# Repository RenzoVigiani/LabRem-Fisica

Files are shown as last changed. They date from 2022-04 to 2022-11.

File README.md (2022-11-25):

# Laboratorios de Física básica
En este readme se detallan las partes mas importantes del proyecto de remotización del laboratorio de física básica, haciendo énfacis en el hardware.

## Protocolo para los laboratorios de "Física básica"
Para poder establecer una comunicación entre al api web, generada por el equipo de software del proyecto, y los dispositivos en el laboratorio establecemos un protocolo en común. 

El procedimiento de comunicación es el siguiente. Cada vez que se quiere modificar algun dato en el laboratorio. El Servidor debe enviar un:
```Ruby 
POST /HTTP/1.1 + <JSON a enviar>
```
#### Json a enviar (ejemplo)
```Ruby  
{ "Estado": [0,true,false],"Analogico": [1,125,542,2]}
```
Y para obtener avances de los datos o reporte de los datos debe enviar un:
```Ruby 
GET /HTTP/1.1
```
De esta forma el Arduino responde ante una petición.

#### Json a recibir (ejemplo)

```Ruby  
{ "Estado": [0,true,false],"Analogico": [1,125,542,2], "Error": "Mensaje de error"}
```

## Sintaxis

**Estado:** Es un array conformado por 3 elementos en el siguiente orden: [Laboratorio, SubLab, Inicio del experimento]

|Laboratorio  | Sub Laboratorio  | Inicio del experimento | Laboratorio Seleccionado | Estado del experimento|
|-|-----|-----|-----------------|--------|
|3|true |true |Lente Convergente|Inicia  |
|3|true |false|Lente Convergente|Finaliza|
|3|false|true |Lente Divergente |Inicia  |
|3|false|false|Lente Divergente |Finaliza|

**Elementos por Laboratorio**

***Convergente***

- Analogico: [Tipo_Diafragma,Distancia_FL,Distancia_LP]
    
    Distancia_FL: Corresponde a la distancia entre Foco y Lente.
    
    Distancia_LP: Corresponde a la distancia entre Lente y Pantalla.

- Tipo_Diafragma = Indica el tipo de diafragma
  - 0 : Sin diafragma
  - 1 : Central
  - 2 : Periferico
  - 3 : Filtro Rojo

***Divergente***

```Ruby 
Analogico:[Tipo_Diafragma, Distancia_FL1, Distancia_L2P, Distancia_L1L2]
```
- Distancia_FL1: Corresponde a la distancia entre Foco y Lente Divergente.
- Distancia_L2P: Corresponde a la distancia entre Lente convergente y Pantalla.
- Distancia_L1L2: Corresponde a la distancia entre Lente divergente y convergente.

## Valores permitidos

Los valores permitidos en las distancias son:

| Distancia          |Valor mín|Valor máx| Unidad |
| ------------------ |---------|---------|--------|
|FL: Foco Lente      |   120   |   970   |  [mm]  |
|LP: Lente Pantalla  |    70   |   970   |  [mm]  |
|FL1: Foco Lente1    |    50   |   920   |  [mm]  |
|L1L2: Lente1 Lente2 |    70   |   900   |  [mm]  |
|L2P: Lente2 Pantalla|    70   |   970   |  [mm]  |

Se puede observar en la imagen las distancias especificadas. Se consideran margenes entre los soportes por seguridad.

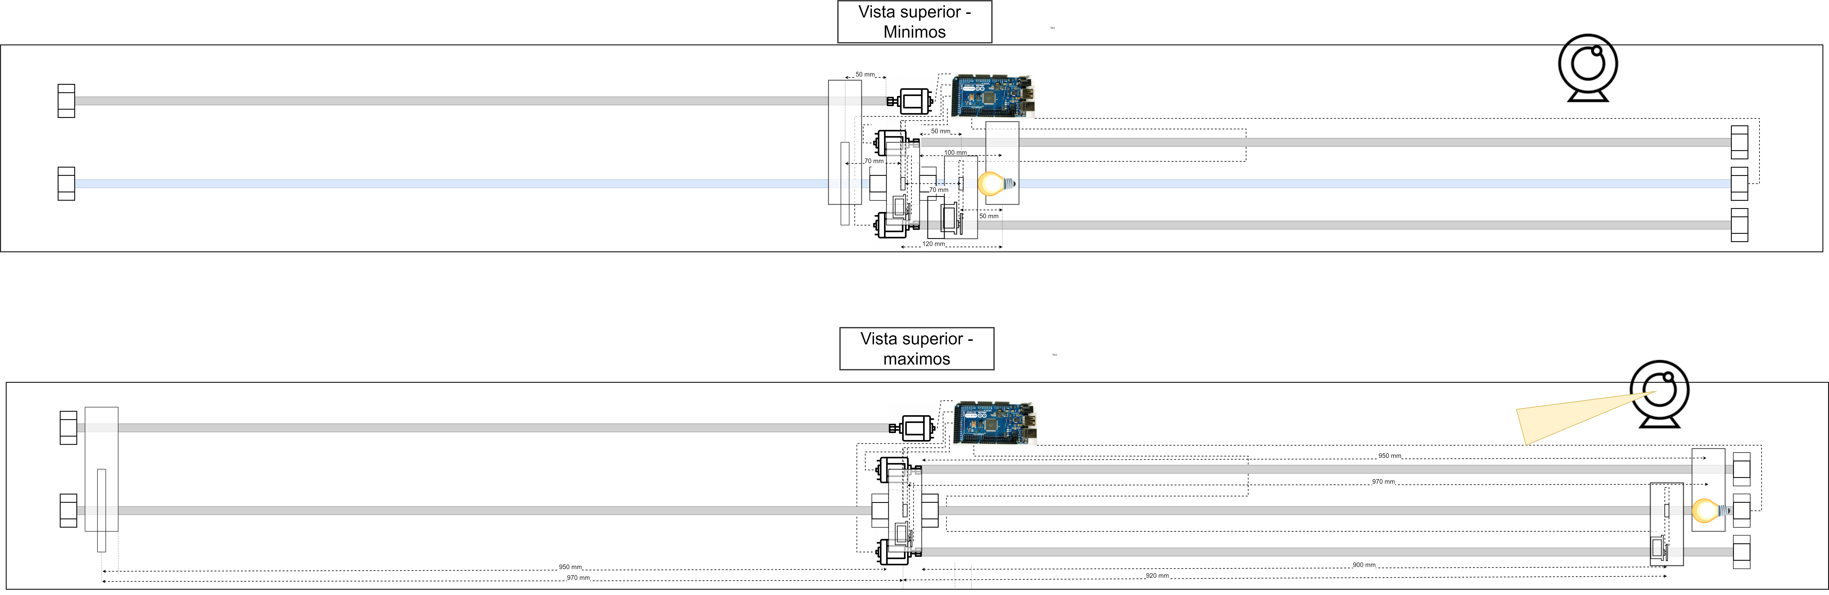
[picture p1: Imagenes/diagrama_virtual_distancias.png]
Vista Superior Distancias


**Error:** Es una variable numerica que representa un mensaje de error. 

| Tipo de error                     |  Valor  |
|-----------------------------------|---------|
| Sin errores                       |    0    |
| Error de distancia                |    1    |
| Error de tipo de diafragma        |    2    |
| Error de laboratorio incorrecto   |    3    |

## Diagramas
Para poder conectar la api web con los actuadores utilizamos un Arduino Mega 2560 y una placa creada por el equipo de hardware. 

Esta placa incorpora todos los drivers e indicadores necesarios para el funcionamiento del laboratorio.

**Arduino Mega 2560: PinOut**
Arduino Mega Pro

||**ESQUEMÁTICO**||
|-|-|-|
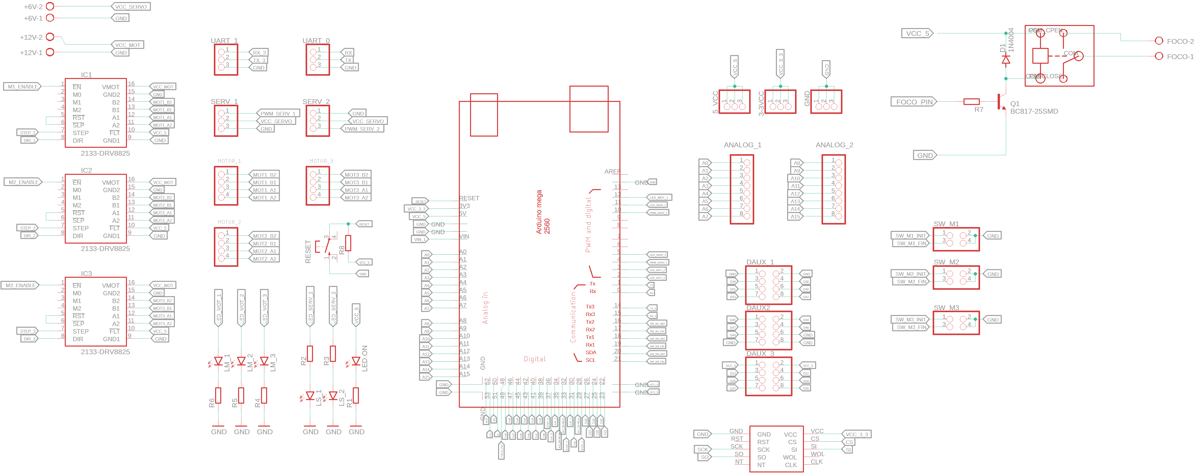
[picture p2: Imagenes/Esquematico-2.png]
Esquematico
||||

||**PCB**||
|-|-|-|
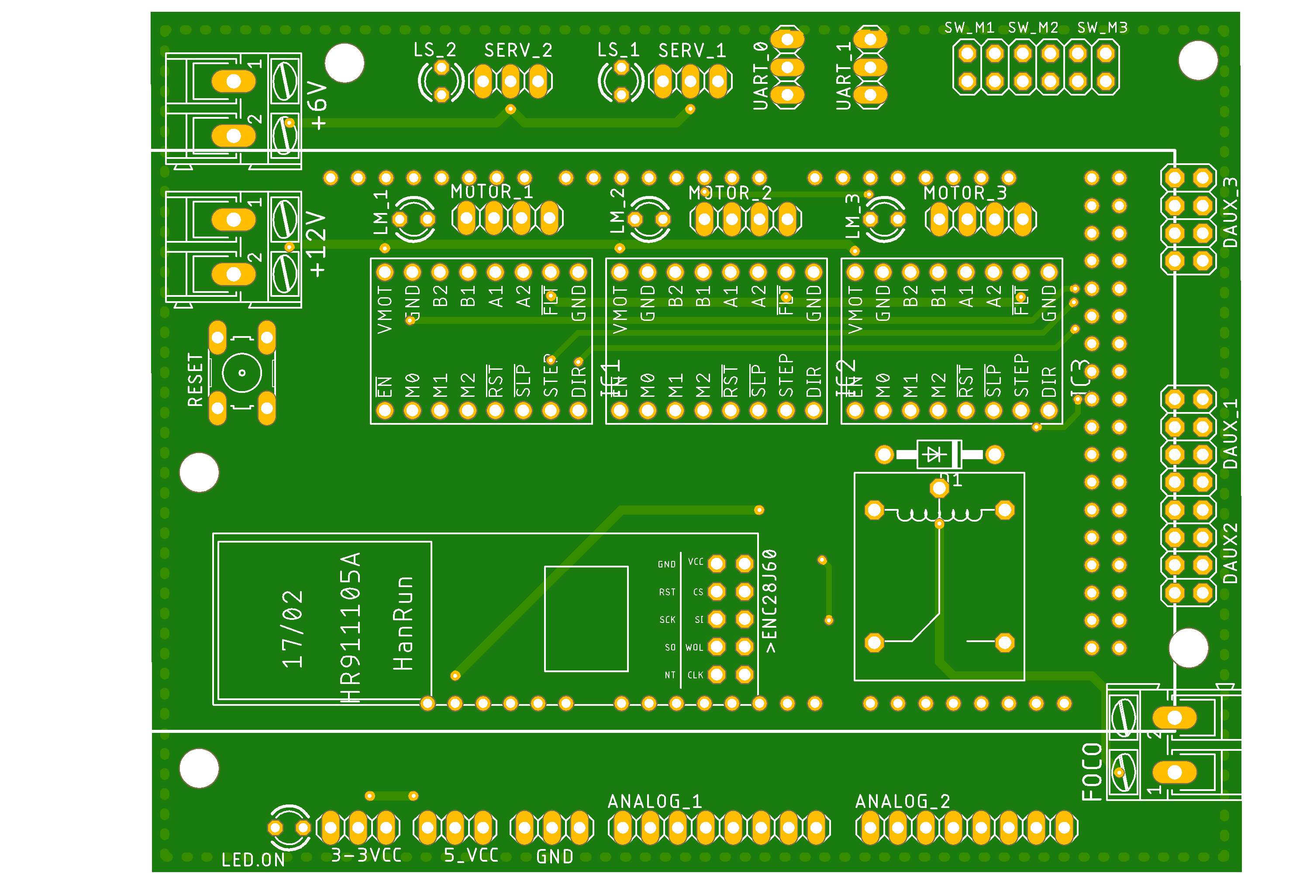
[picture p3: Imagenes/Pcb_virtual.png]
Pcb Virtual
||||
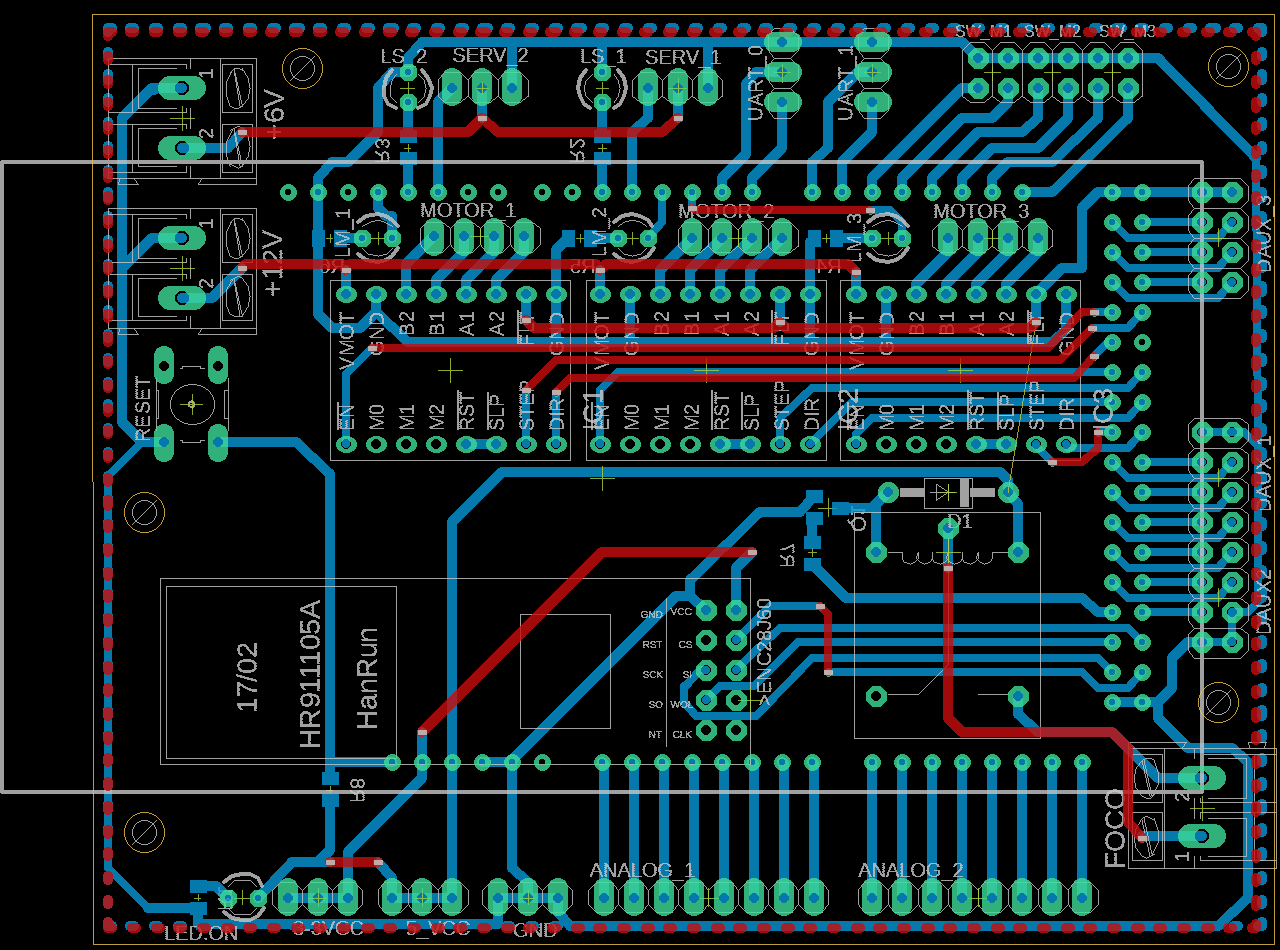
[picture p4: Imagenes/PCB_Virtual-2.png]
Pcb Virtual
||||
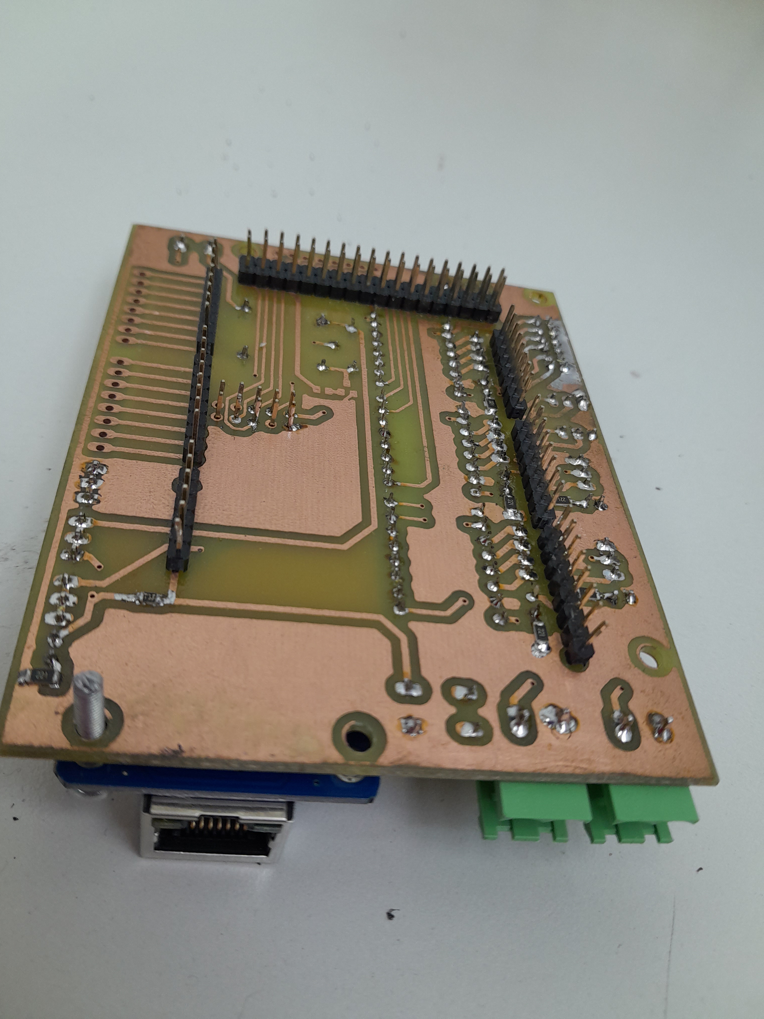
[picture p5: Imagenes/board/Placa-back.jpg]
||||
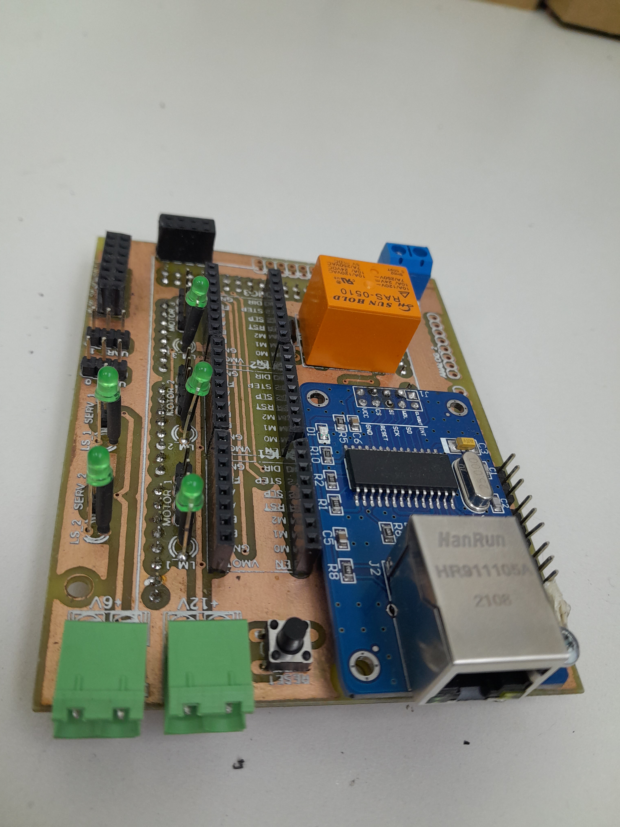
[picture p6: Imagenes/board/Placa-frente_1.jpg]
||||
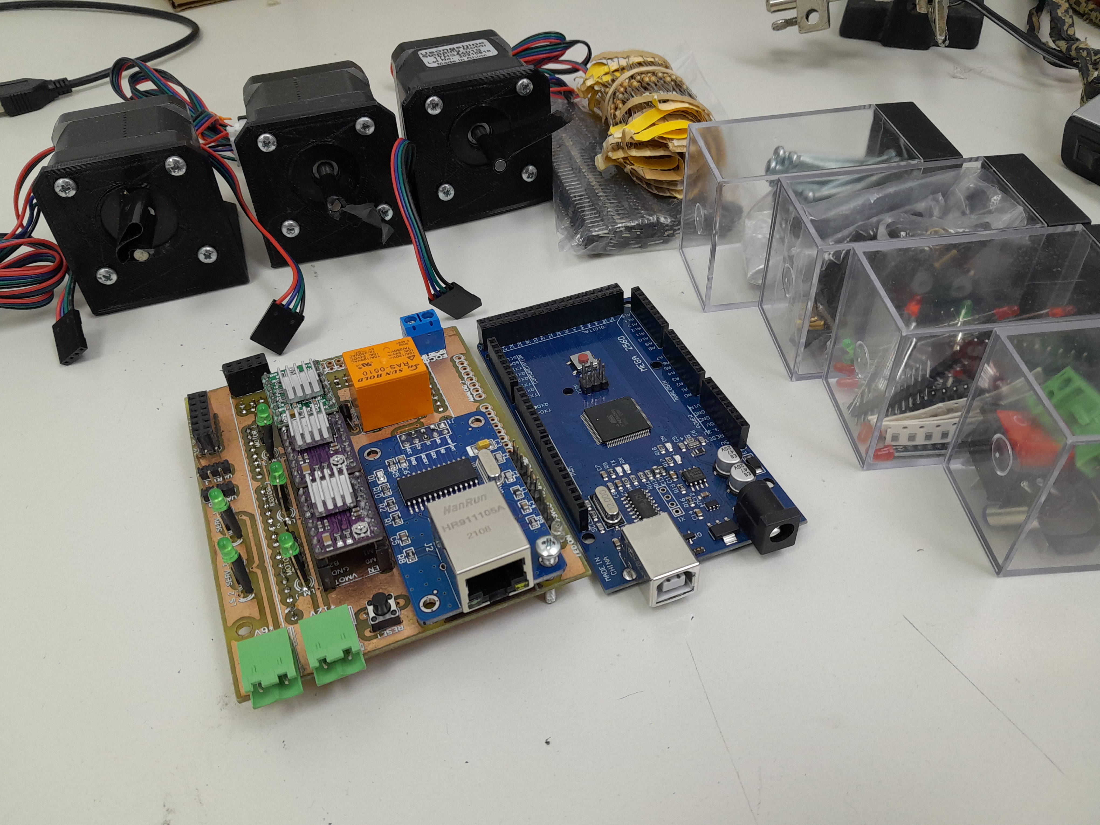
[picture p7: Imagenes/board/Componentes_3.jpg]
||||

**Diagrama general**

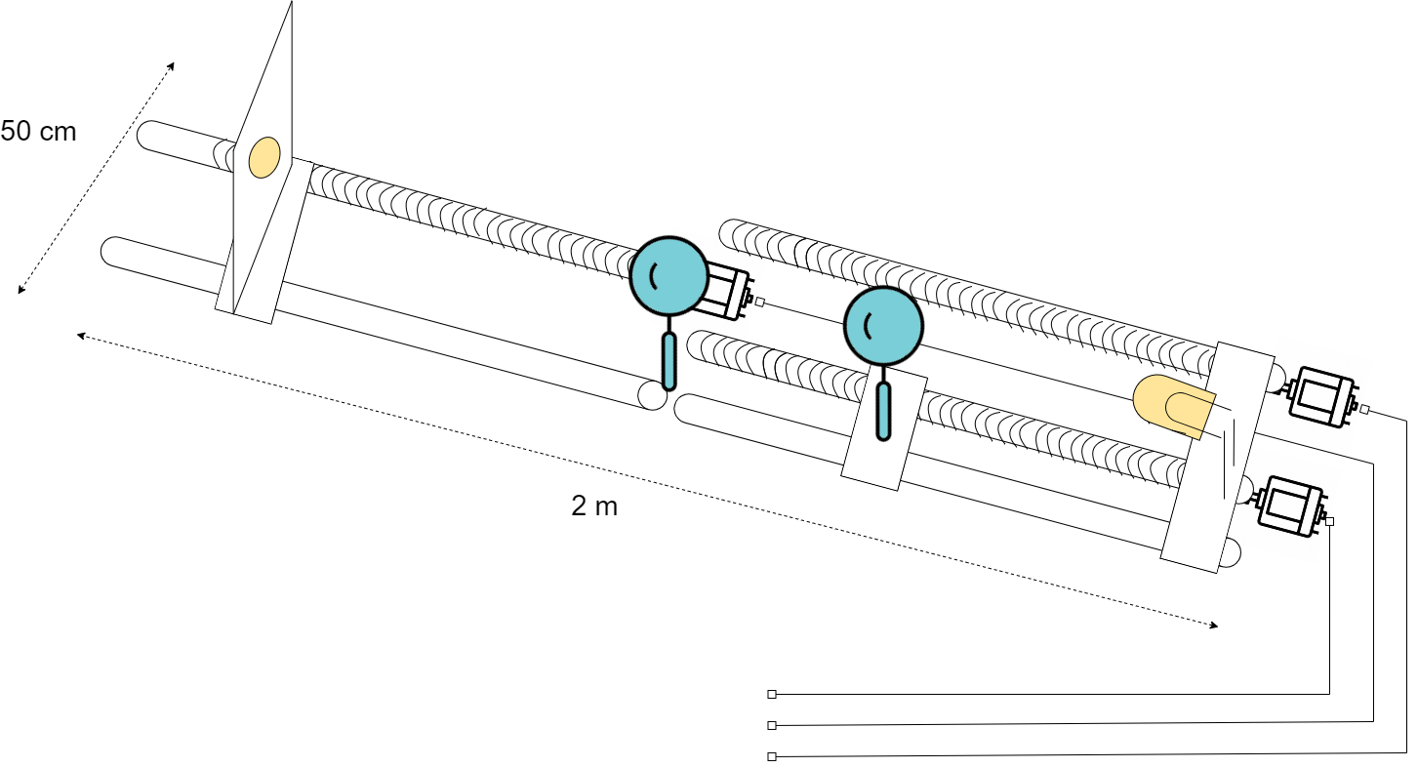
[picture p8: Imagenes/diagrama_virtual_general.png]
Vista General Virtual


**Diagrama Vista superior**

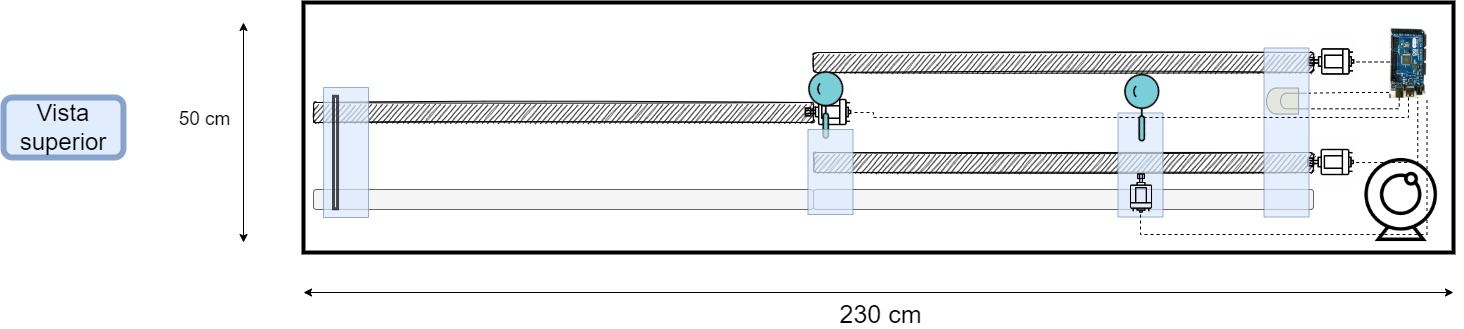
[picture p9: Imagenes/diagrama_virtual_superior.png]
Vista Superior Virtual


**Diagrama Vista frontal**

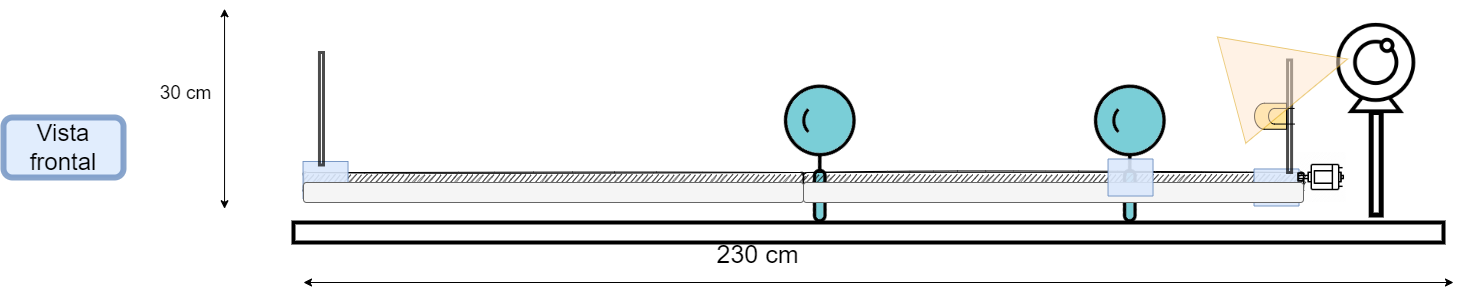
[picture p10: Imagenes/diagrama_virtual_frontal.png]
Vista Frontal Virtual


**Datasheets Actuadores**
- [Recopilación de Datasheets](https://renzovigiani.notion.site/adea4f735c994faaa2f919a7e5105e9d?v=83070c8c05d34c02905fc370e37b802a)
- [Servo Motor MG966R](https://github.com/RenzoVigiani/LabRem-Fisica/blob/main/datasheets/MG996R-Datasheet.pdf)
- [Motor Paso a paso](https://github.com/RenzoVigiani/LabRem-Fisica/blob/main/datasheets/MG996R-Datasheet.pdf)
- [Lampara Led](http://wayjun.com/Datasheet/Led/3W%20High%20Power%20LED.pdf)

**Soportes 3D**

 A continuación se pueden ver los elementos diseñados por el equipo de hardware y luego creados a partir de una impresora 3D. Esto permitió generar soportes y gabinetes de acuerdo a los requerimientos y logrando mayor flexibilidad.

Se pueden ver los soportes creados para el sistema de movimiento de todo el ensayo. Se muestran:
- 4 bases para las lentes y el movimiento sobre los rieles.
- 3 soportes para motores paso a paso.
- 1 gabinete para soporte de foco o fuente de luz.
- 1 soporte para la pantalla.

|            |   |
|-------------------------|---------|
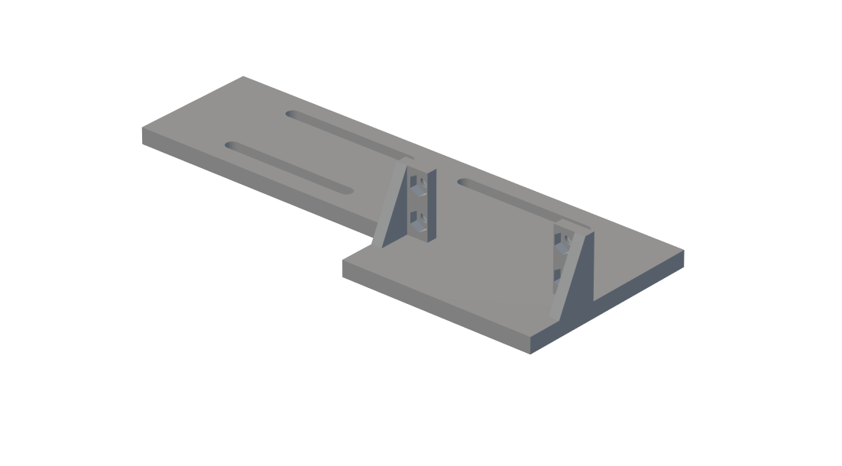
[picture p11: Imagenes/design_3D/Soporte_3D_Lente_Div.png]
Soporte 3D Lente Divergente
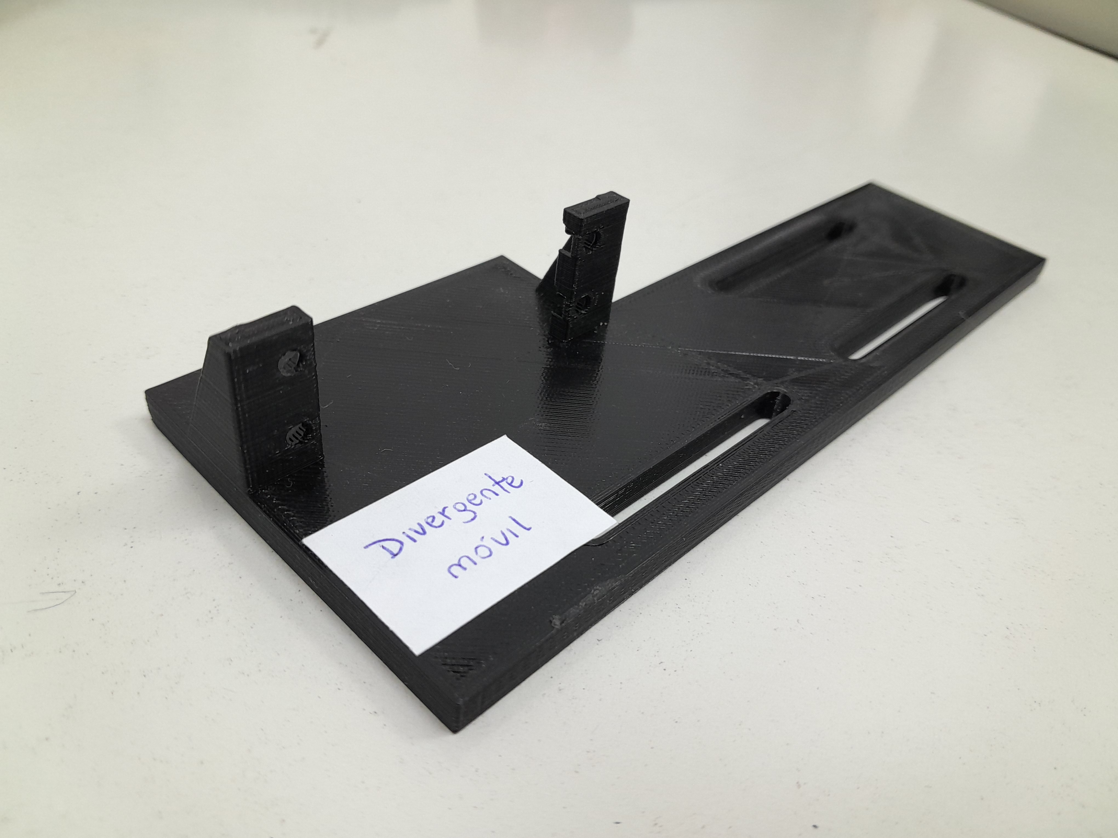
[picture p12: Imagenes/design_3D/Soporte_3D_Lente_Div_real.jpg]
Soporte 3D Lente Divergente Real
|   |    |
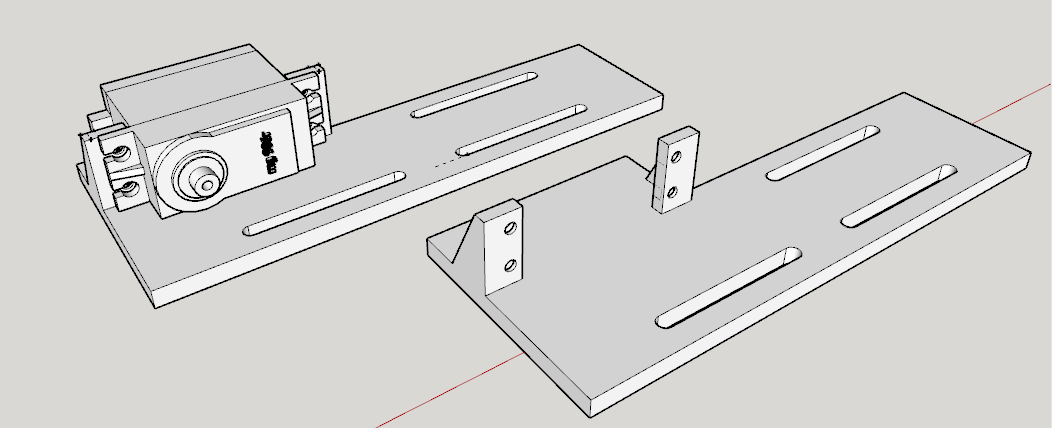
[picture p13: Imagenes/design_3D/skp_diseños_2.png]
Soporte 3D Lente Diafragma
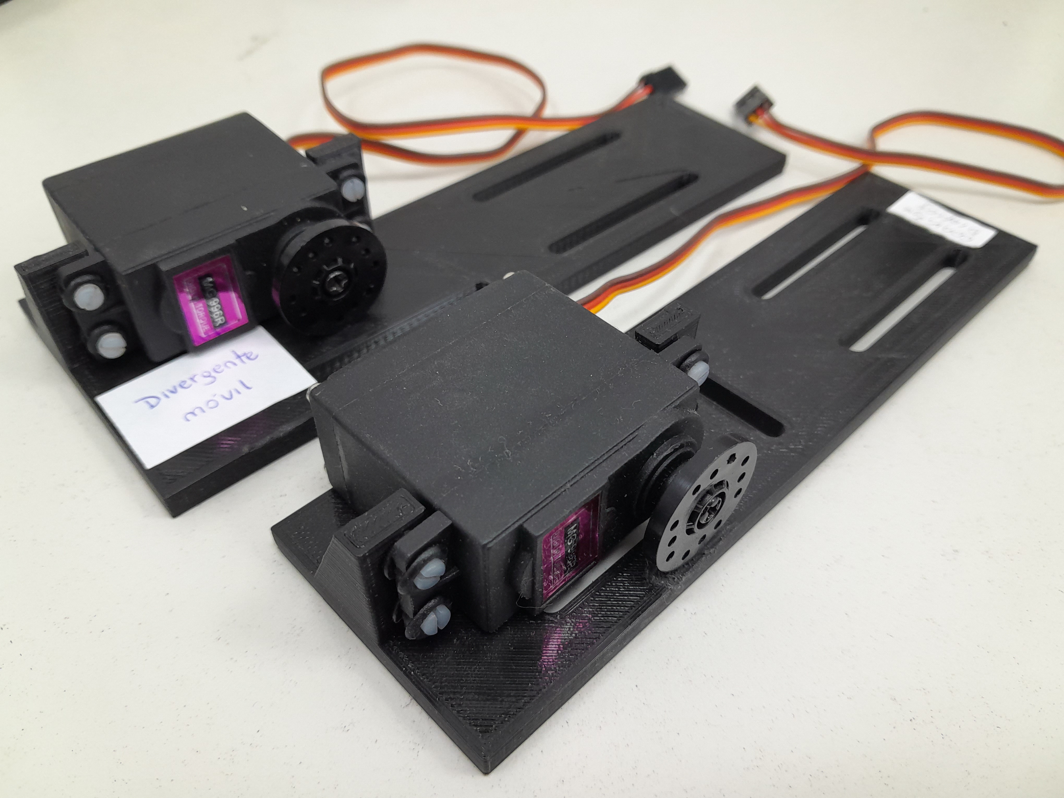
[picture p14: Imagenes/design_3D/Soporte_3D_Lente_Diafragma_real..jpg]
Soporte 3D Lente Diafragma Real
| ||
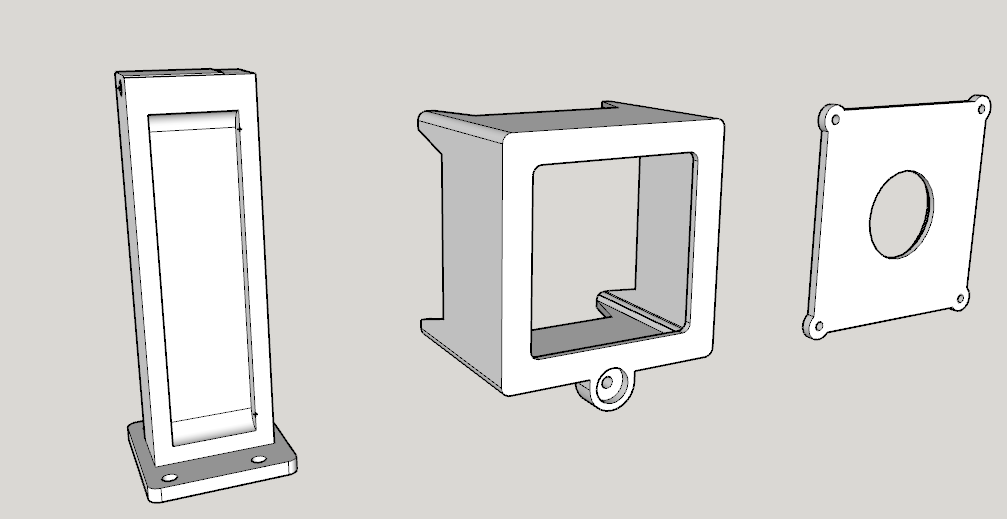
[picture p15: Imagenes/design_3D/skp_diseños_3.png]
Caja Lampara Led
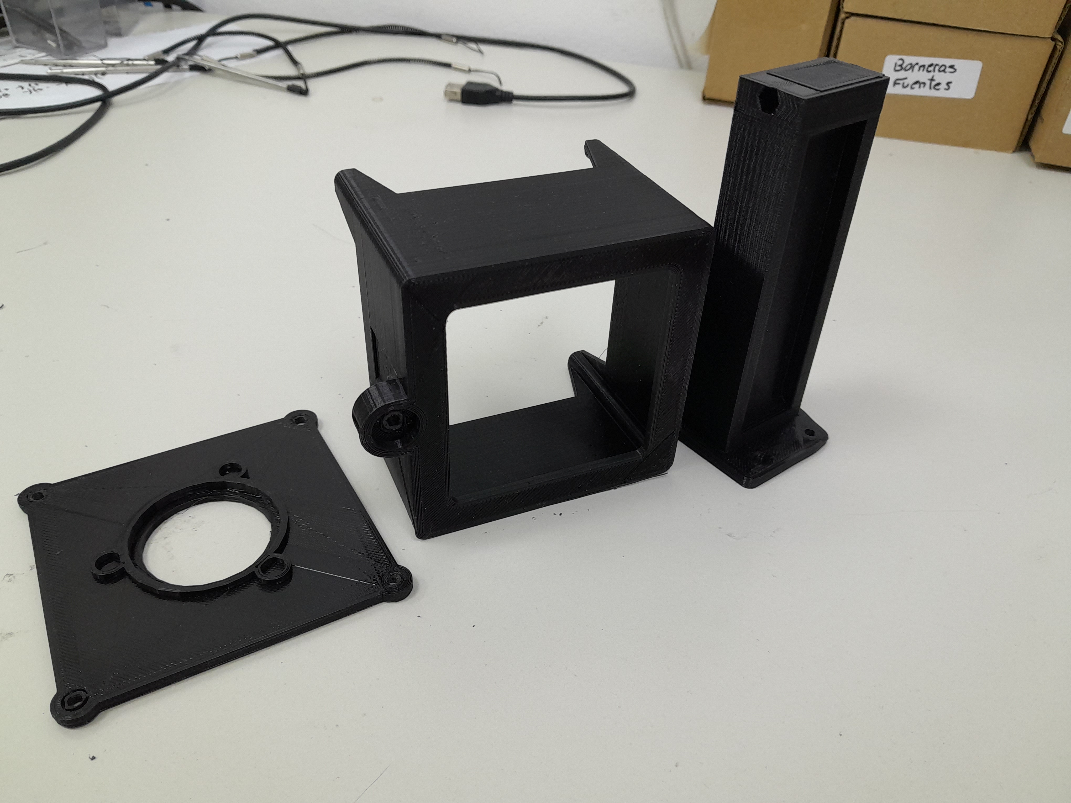
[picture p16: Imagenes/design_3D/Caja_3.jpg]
Caja Lampara Led 2
|   |   |
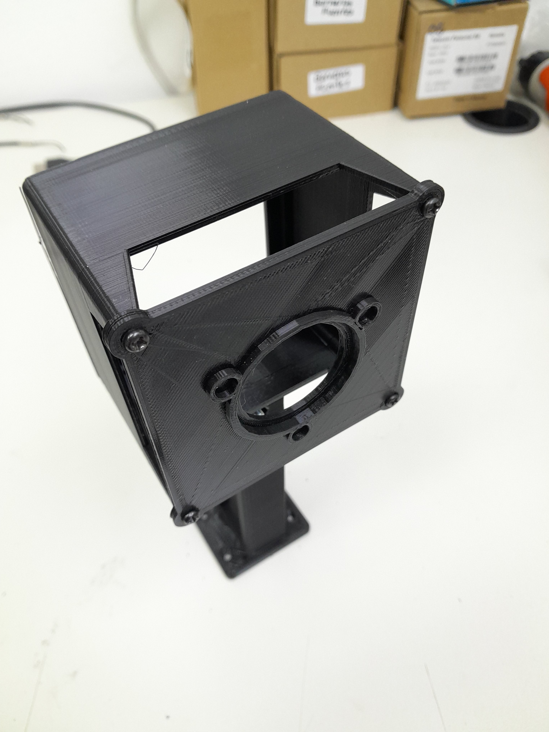
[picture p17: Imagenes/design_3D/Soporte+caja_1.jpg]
Caja Lampara Led Ensamblado
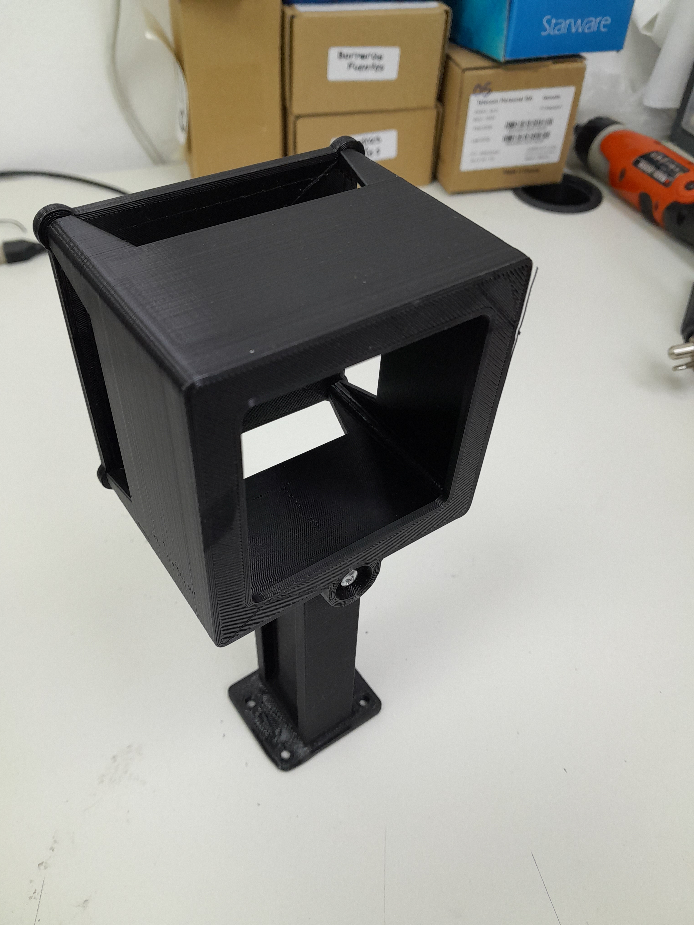
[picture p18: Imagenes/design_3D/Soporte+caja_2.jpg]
Caja Lampara Led Ensamblado 2
|  |  |
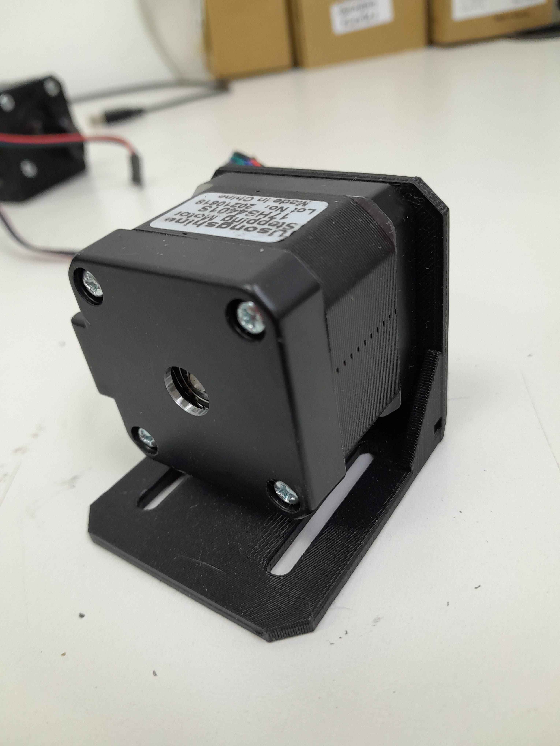
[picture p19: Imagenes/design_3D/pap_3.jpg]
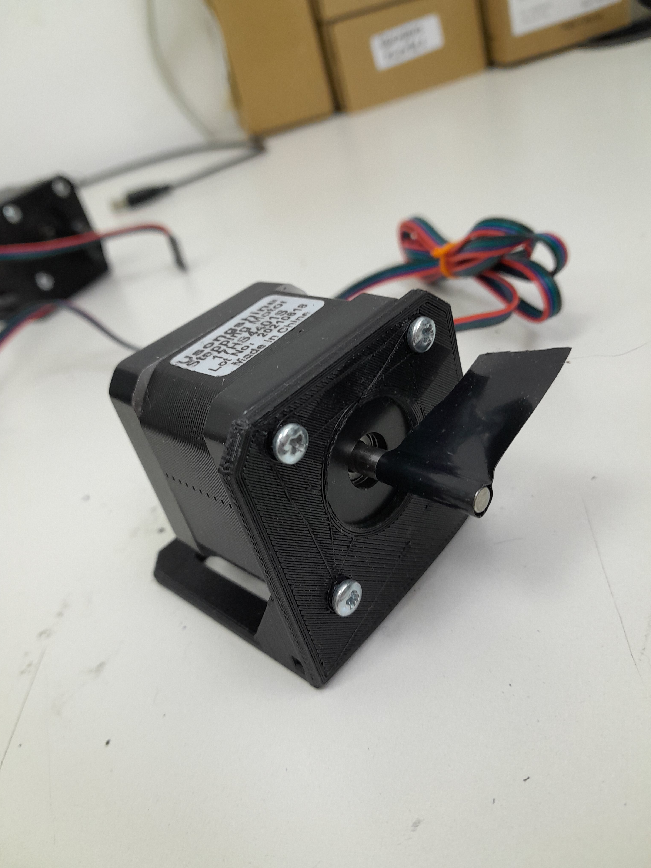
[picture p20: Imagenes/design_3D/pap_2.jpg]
|  |  |
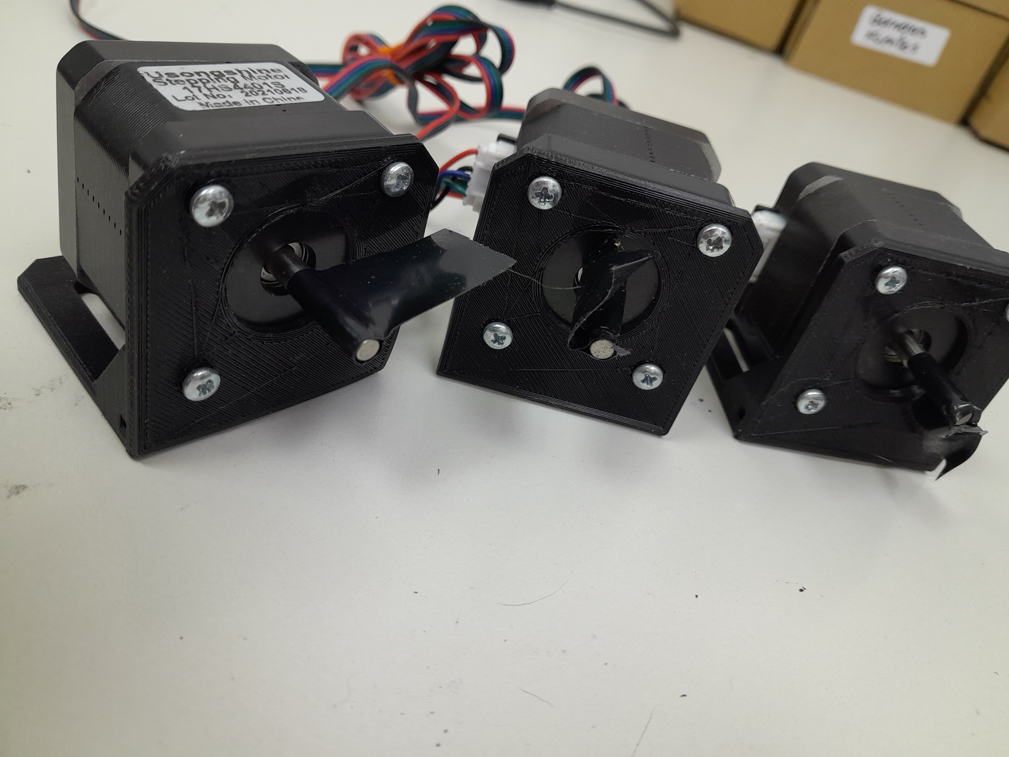
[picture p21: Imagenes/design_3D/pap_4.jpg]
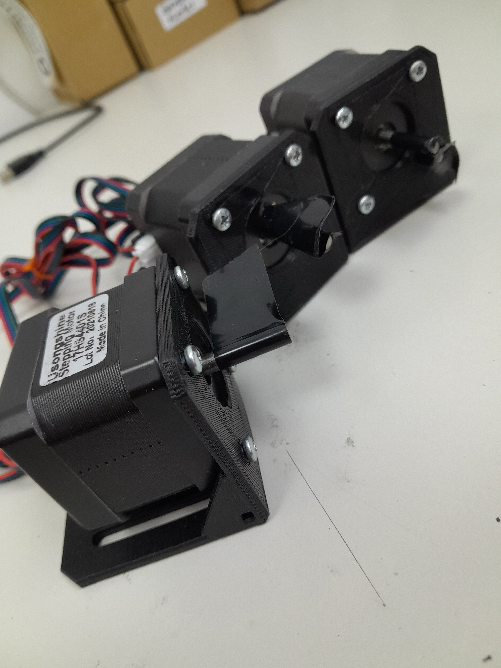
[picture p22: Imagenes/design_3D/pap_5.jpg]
|  |  |

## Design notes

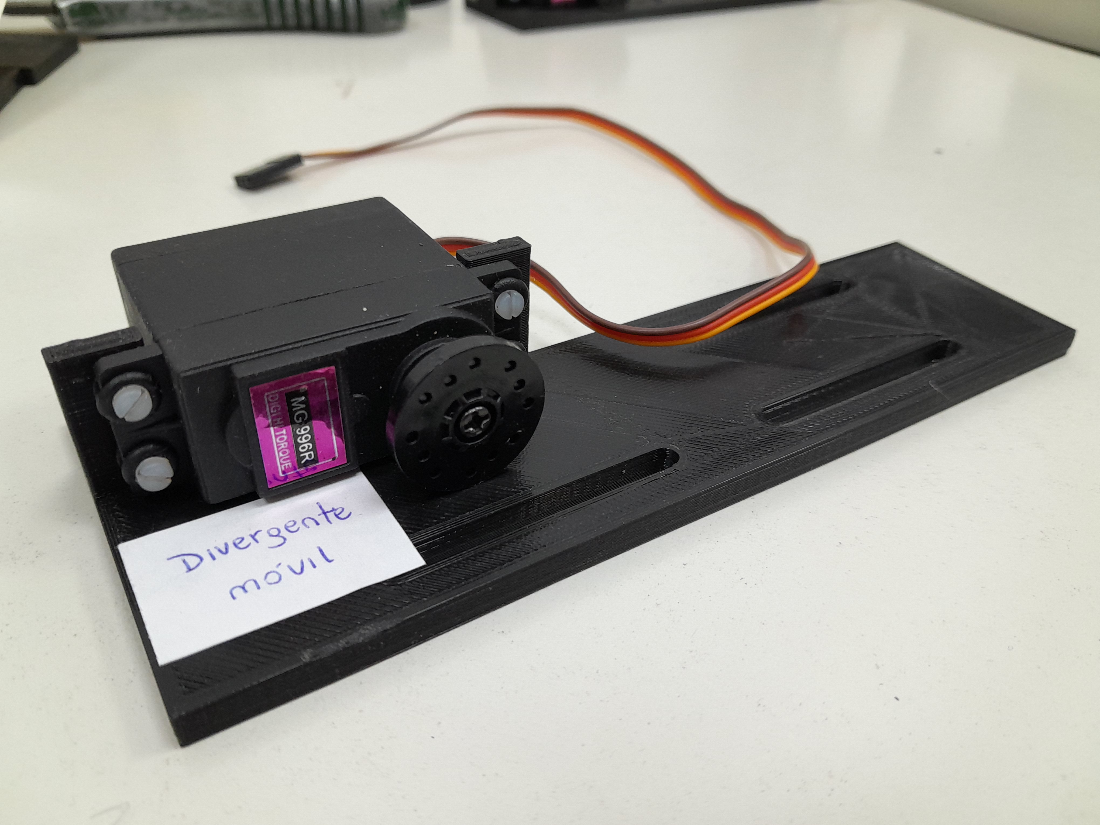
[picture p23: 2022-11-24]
Imagenes/design_3D/Base_servo_2.jpg

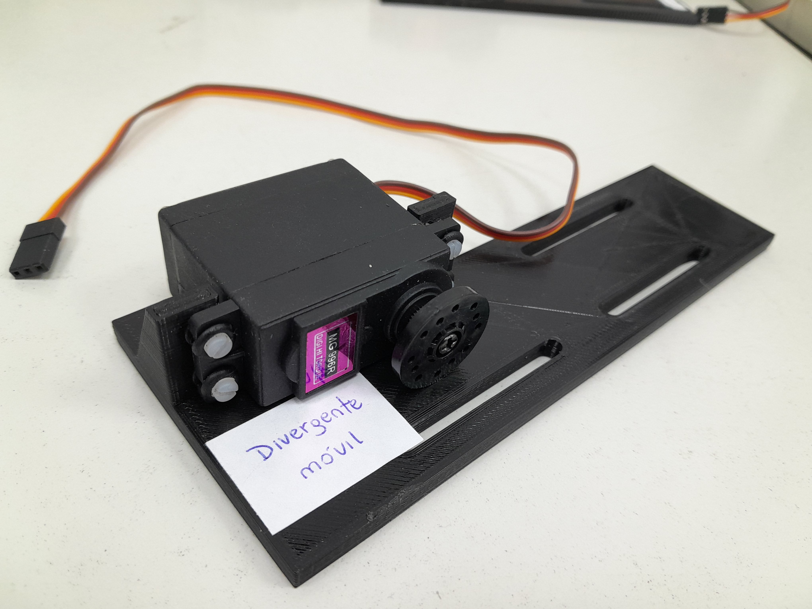
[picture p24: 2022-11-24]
Imagenes/design_3D/Base_servo_3.jpg

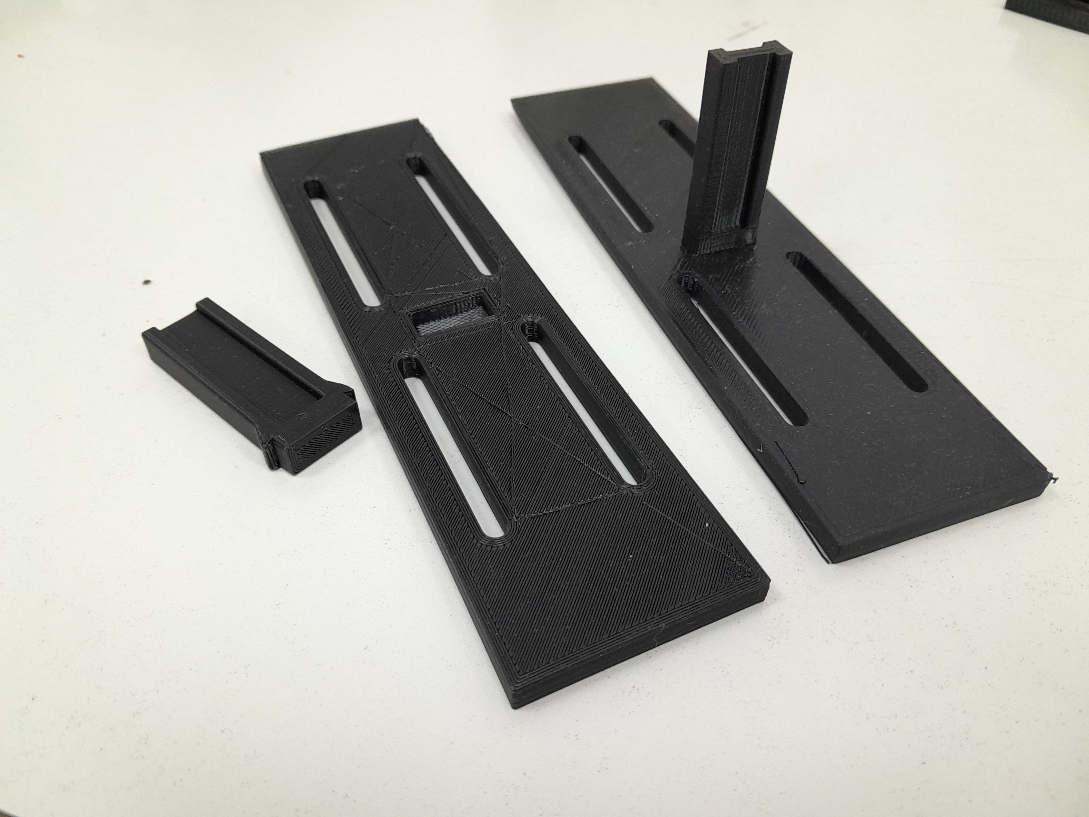
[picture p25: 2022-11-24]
Imagenes/design_3D/Base_lente1.jpg

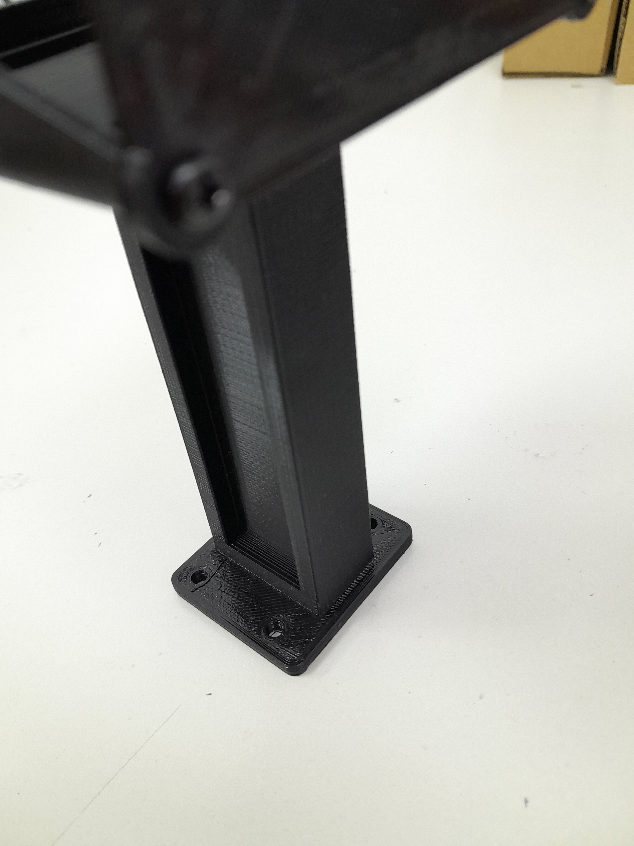
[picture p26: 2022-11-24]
Imagenes/design_3D/Soporte+caja_3.jpg

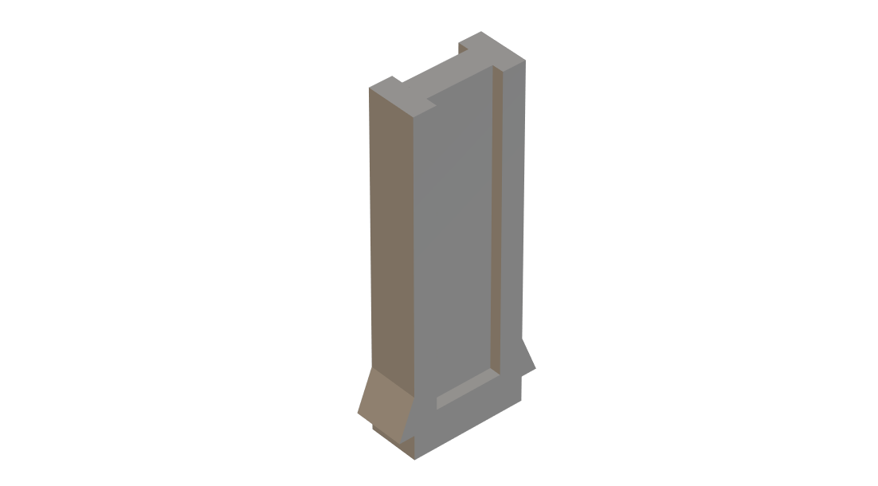
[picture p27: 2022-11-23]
Imagenes/design_3D/Soporte_3D_barra_central.png

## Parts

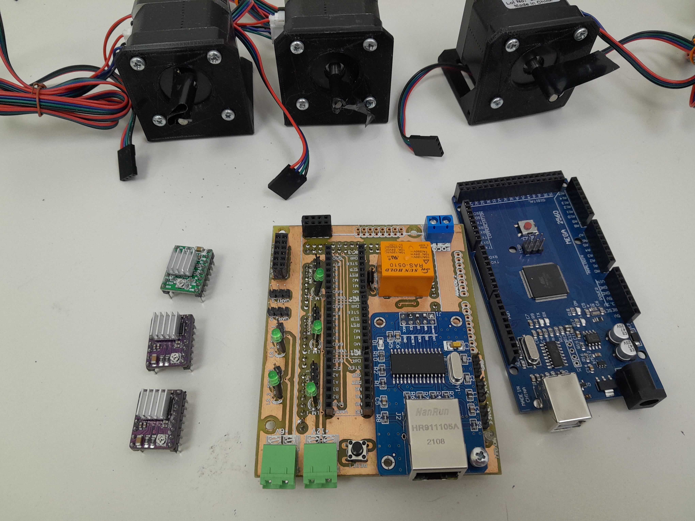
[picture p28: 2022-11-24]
Imagenes/board/Componentes_2.jpg

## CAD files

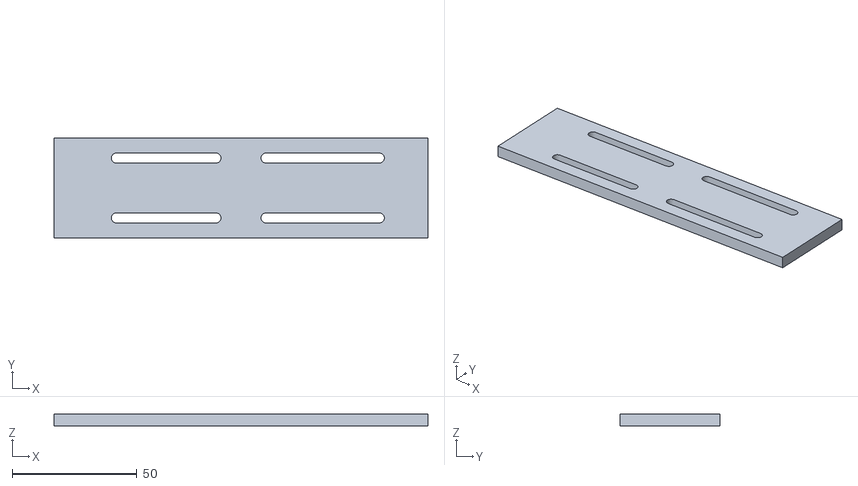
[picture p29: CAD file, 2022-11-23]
Impresion_3D/LuzBarra.stl
150.0 x 40.0 x 5.00

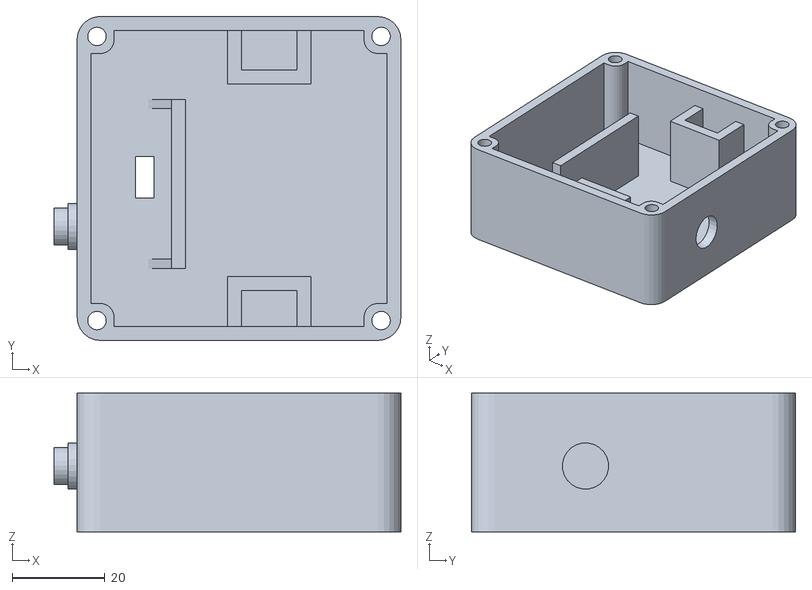
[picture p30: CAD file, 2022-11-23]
Impresion_3D/Caja.stl
75.0 x 70.0 x 30.0

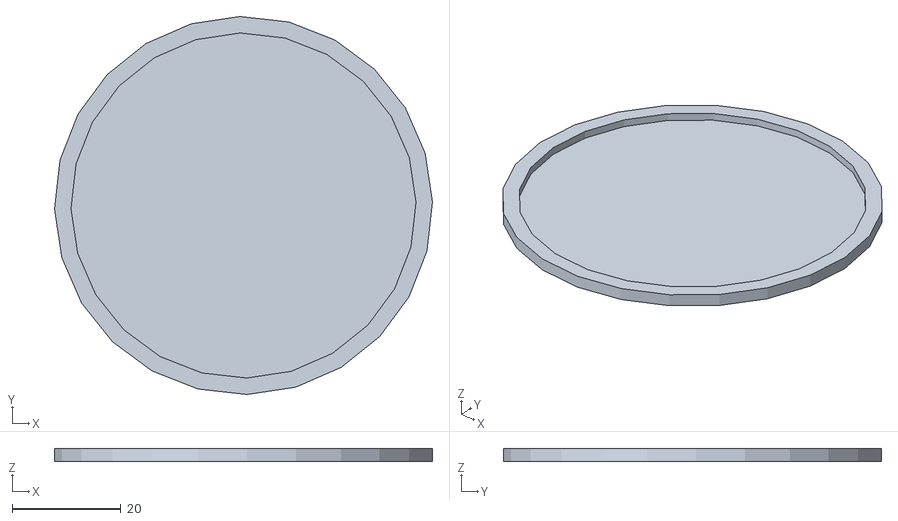
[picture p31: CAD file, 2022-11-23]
Impresion_3D/Difusor.stl
69.4 x 69.4 x 2.30

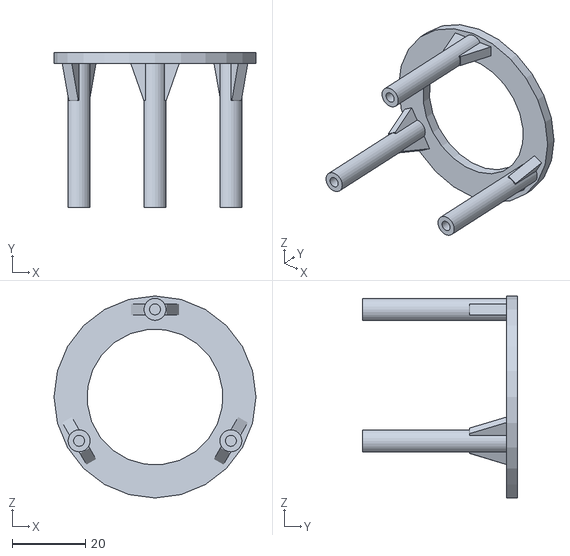
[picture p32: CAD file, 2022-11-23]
Impresion_3D/LuzPorta.stl
55.0 x 42.2 x 55.0

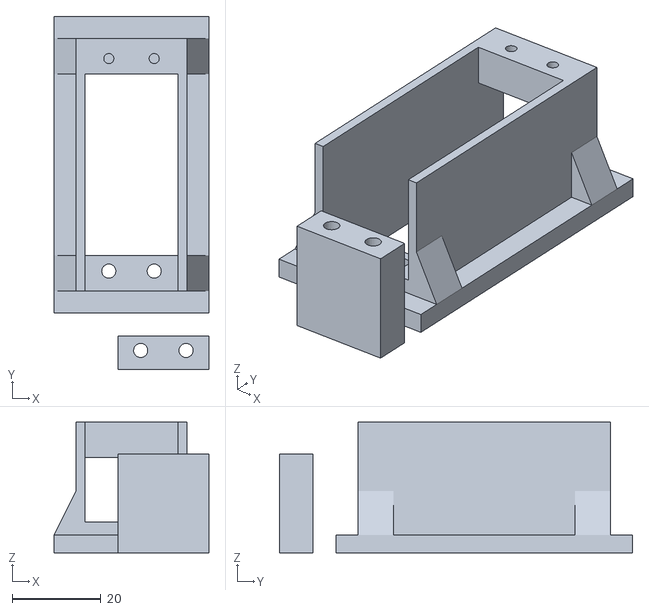
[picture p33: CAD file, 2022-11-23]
Impresion_3D/TelecoServo.stl
35.0 x 79.7 x 29.5

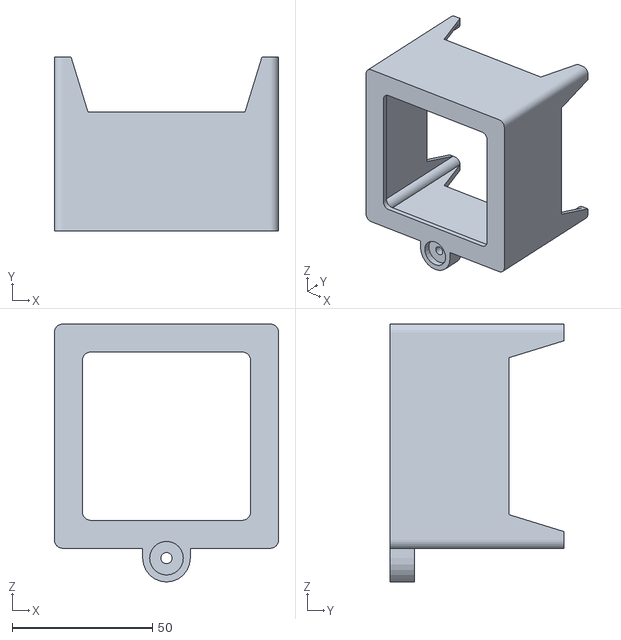
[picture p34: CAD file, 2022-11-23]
Impresion_3D/LuzFrente.stl
80.0 x 61.9 x 92.0

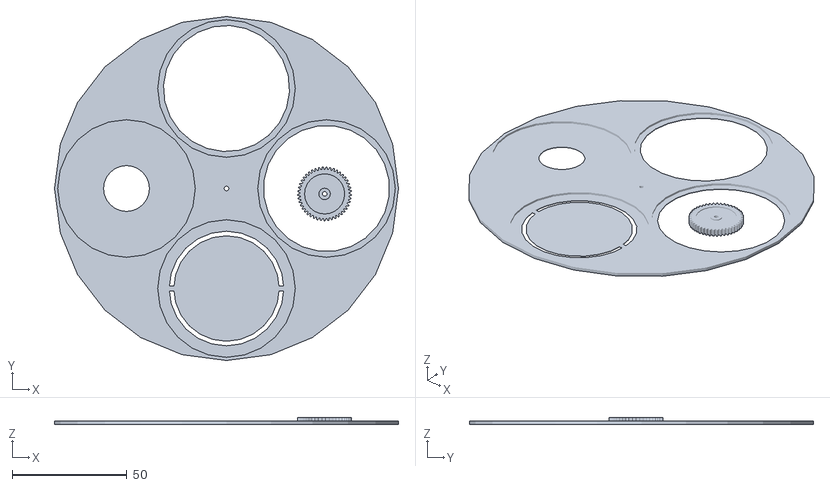
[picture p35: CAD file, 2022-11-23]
Impresion_3D/diafragma-con-engranaje.stl
150.0 x 150.0 x 3.00

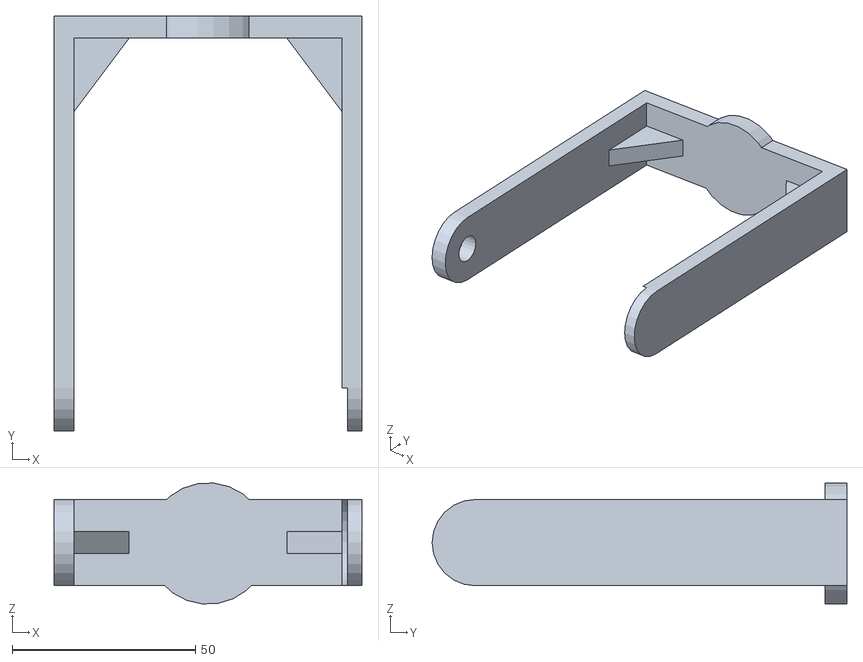
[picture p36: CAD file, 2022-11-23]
Impresion_3D/SoporteCaja.stl
84.0 x 113.1 x 33.0

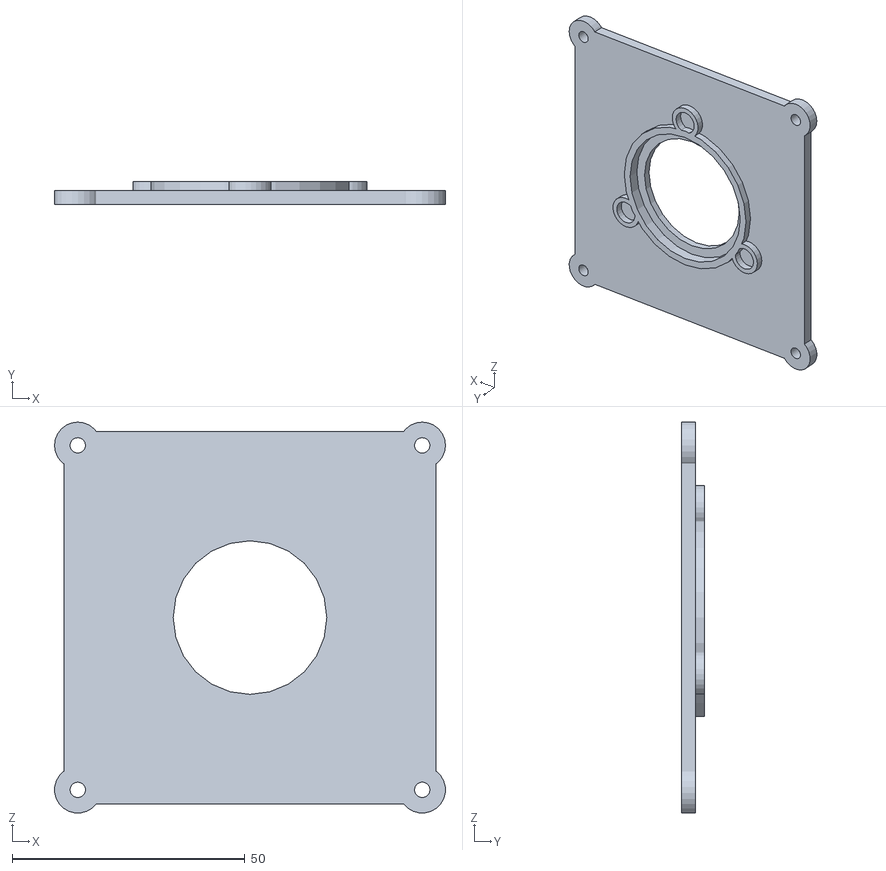
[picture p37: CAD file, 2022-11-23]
Impresion_3D/LuzTrasera.stl
84.0 x 5.00 x 84.0

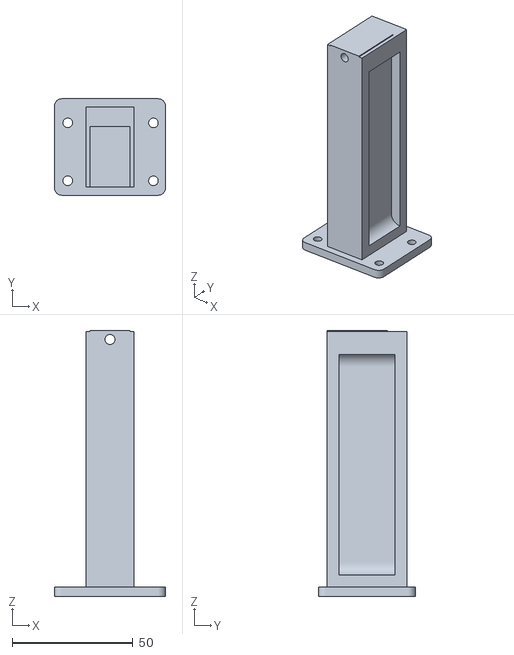
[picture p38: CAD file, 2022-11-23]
Impresion_3D/LuzPoste.stl
46.0 x 40.0 x 110.2

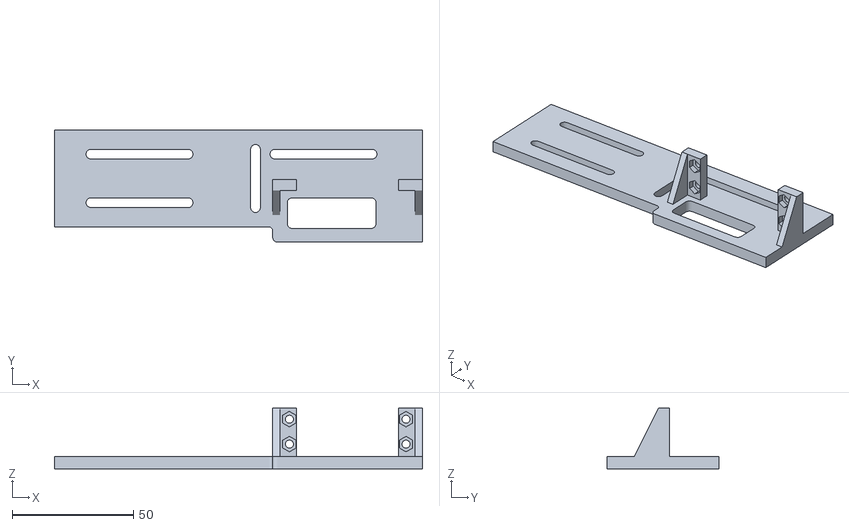
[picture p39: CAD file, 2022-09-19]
Impresion_3D/Barra_10x4_LyD.stl
151.5 x 46.2 x 25.0

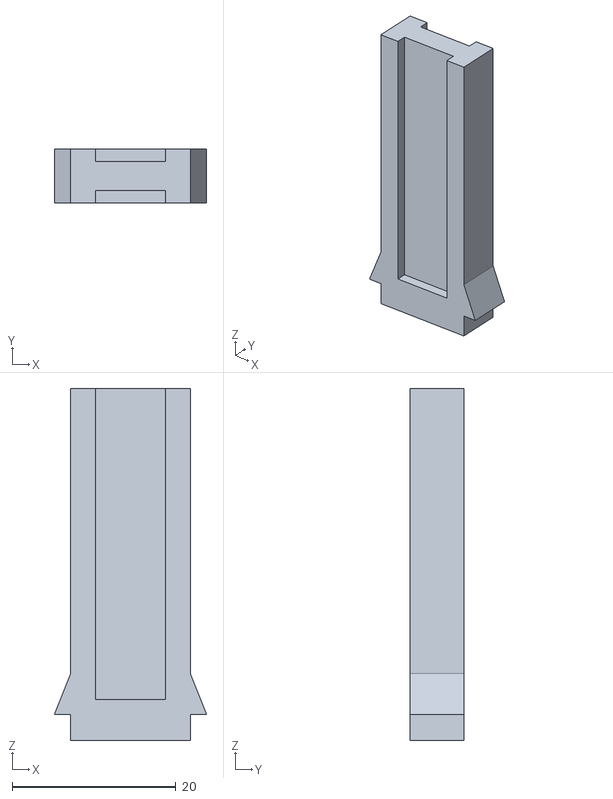
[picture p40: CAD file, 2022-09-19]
Impresion_3D/BarraInterna.stl
18.6 x 6.60 x 43.0

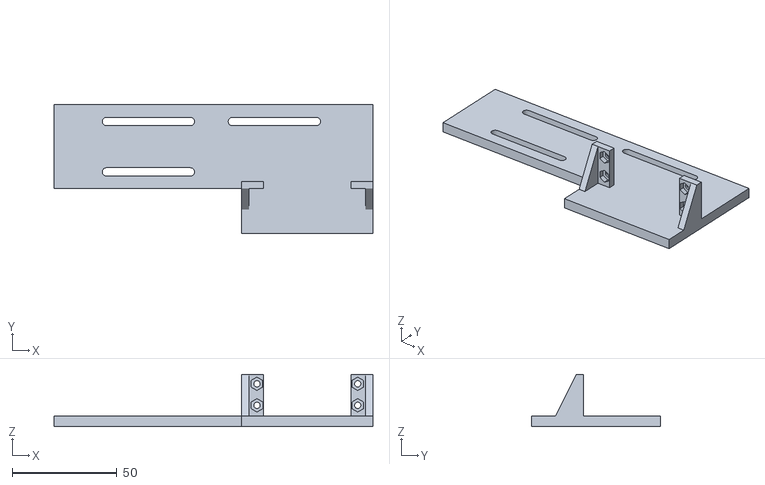
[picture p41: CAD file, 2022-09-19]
Impresion_3D/Barra_10x4_V2.stl
152.0 x 61.2 x 25.0

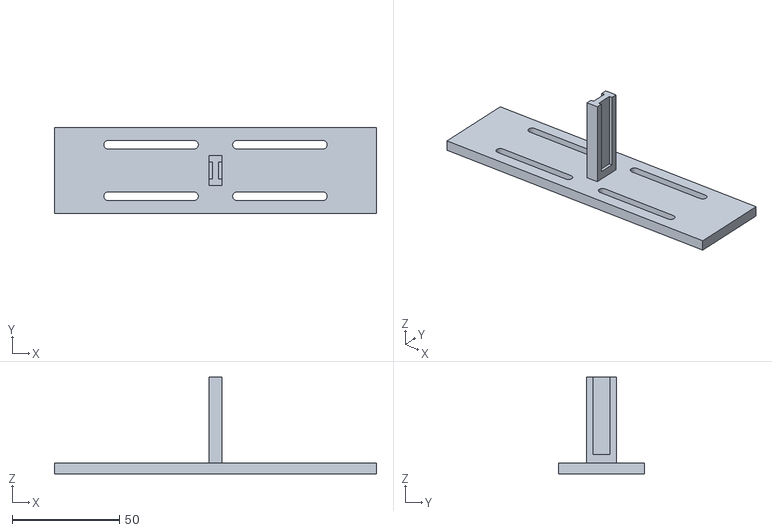
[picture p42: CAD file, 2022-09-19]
Impresion_3D/Barra_15x4.stl
150.0 x 40.0 x 45.0

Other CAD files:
Esquematico_y_PCB/Diseño de FISICA v19.f3z
Esquematico_y_PCB/Diseño de FISICA v2.f3z
Esquematico_y_PCB/Diseño de FISICA v8.f3z
Impresion_3D/14b+engranaje+45+dientes.skp
Impresion_3D/828_DELUX_3D-DRAWINGS.skp
Impresion_3D/BarraInterna.skp
Impresion_3D/Barra_10x4.skp
Impresion_3D/Barra_10x4_LyD.skp
Impresion_3D/Barra_10x4_V2.skp
Impresion_3D/Barra_15x4.skp
Impresion_3D/Caja.skp
Impresion_3D/CajaCompleto.skp
Impresion_3D/Difusor.skp
Impresion_3D/LuzBarra.skp
Impresion_3D/LuzCompleta.skp
Impresion_3D/LuzFisica.skp
Impresion_3D/LuzFrente.skp
Impresion_3D/LuzPorta.skp
Impresion_3D/LuzPoste.skp
Impresion_3D/LuzTrasera.skp
Impresion_3D/SoporteCaja.skp
Impresion_3D/TelecoServo.skp

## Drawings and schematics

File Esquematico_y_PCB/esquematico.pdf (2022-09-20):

# 2133-DRV8825

# BC817-25SMD ¹N⁴⁰⁰⁴

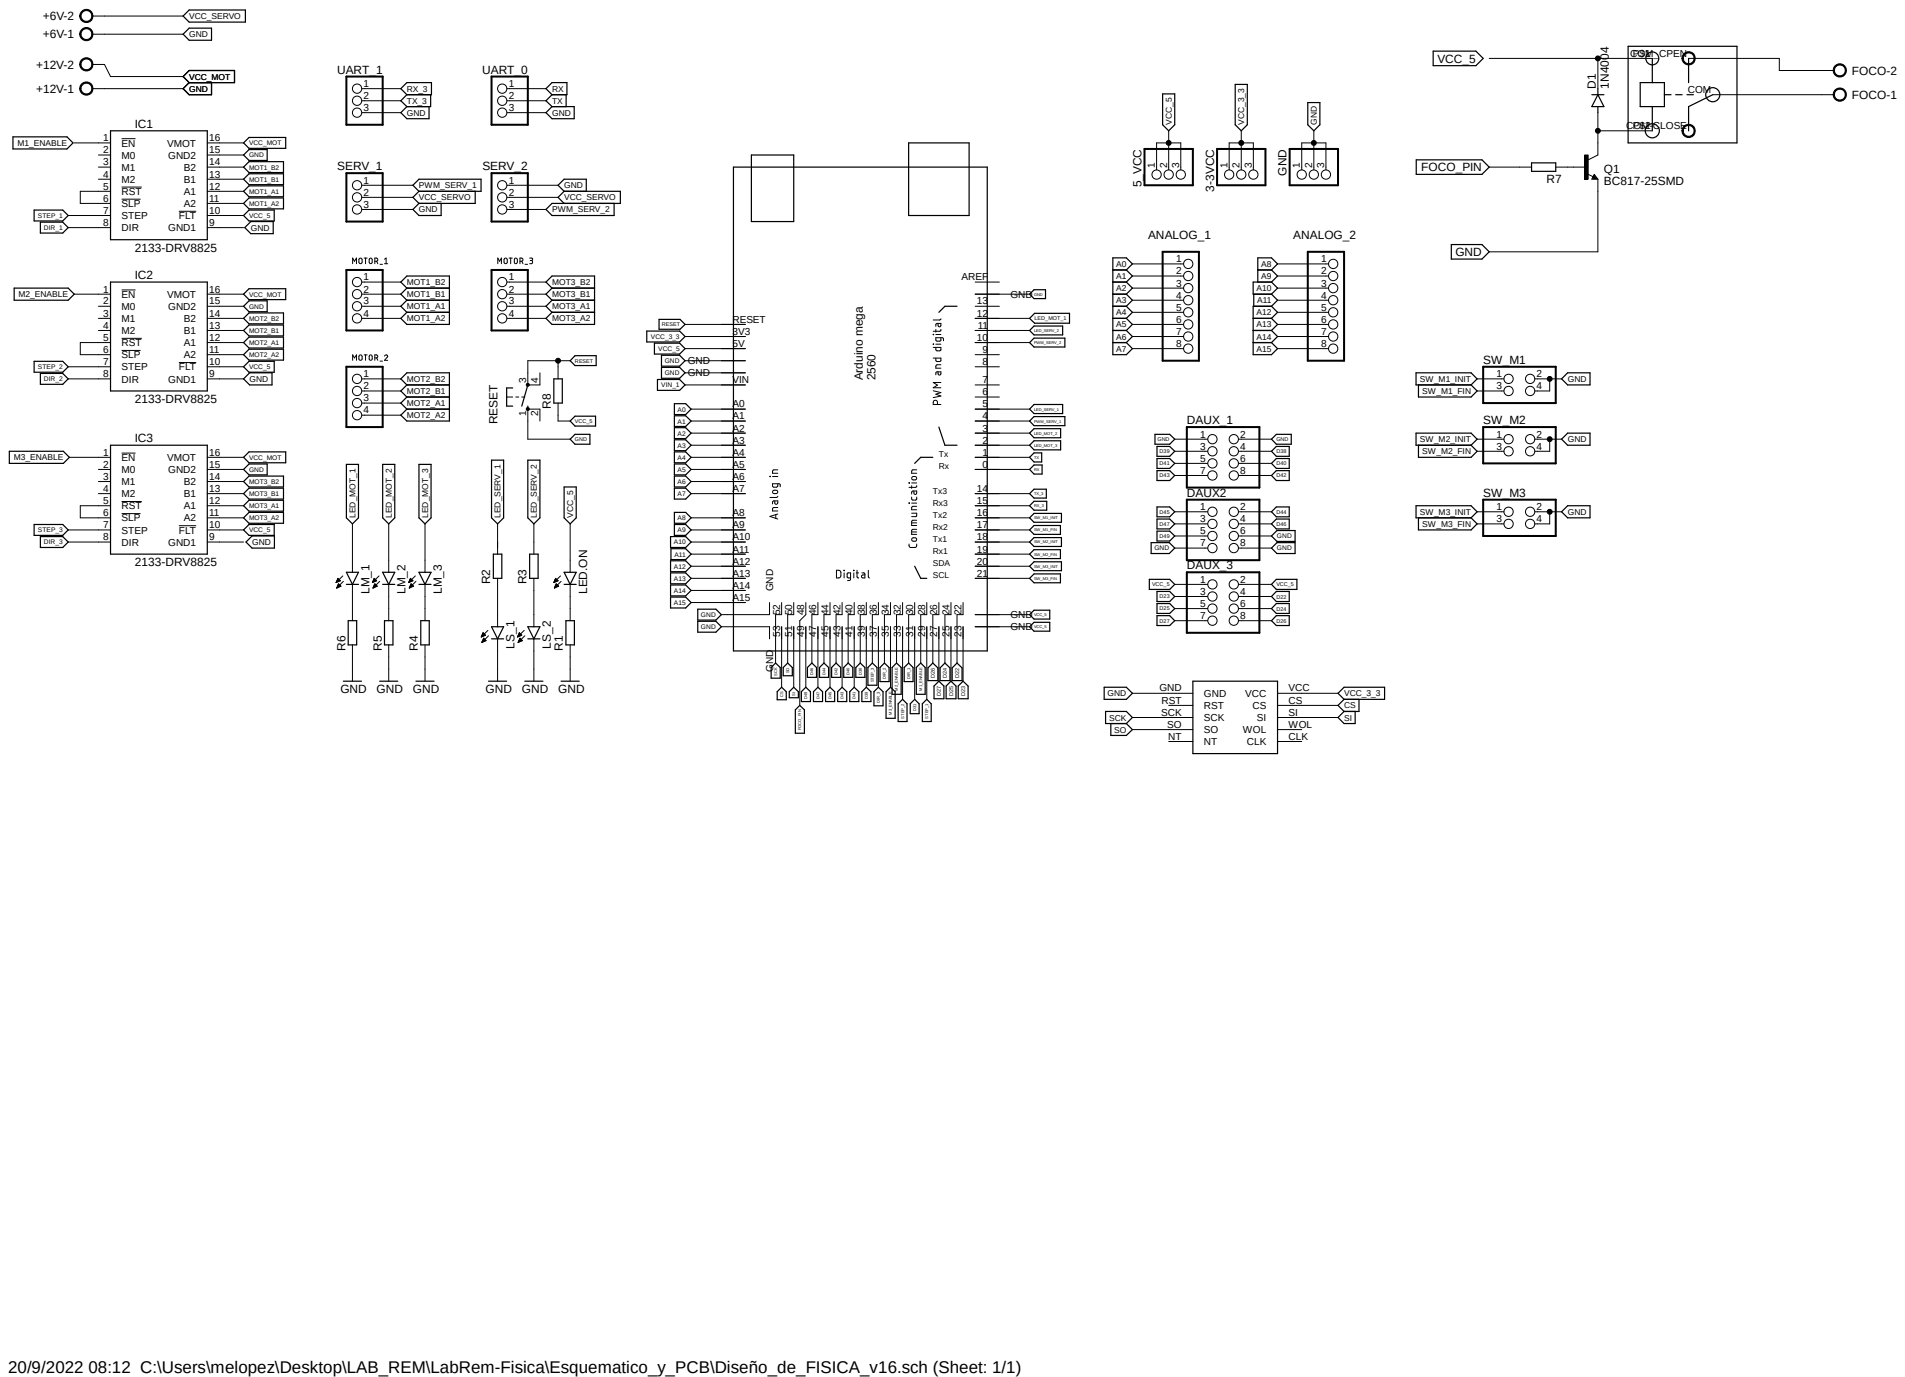
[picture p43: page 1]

VCC_5
GND GND

21 GND GND 53514947454341393735333129272523 GND ⁵²⁵⁰⁴⁸⁴⁶⁴⁴⁴²⁴⁰³⁸³⁶³⁴³²³⁰²⁸²⁶²⁴²² GND

20/9/2022 08:12 C:\Users\melopez\Desktop\LAB_REM\LabRem-Fisica\Esquematico_y_PCB\Diseño_de_FISICA_v16.sch (Sheet: 1/1)

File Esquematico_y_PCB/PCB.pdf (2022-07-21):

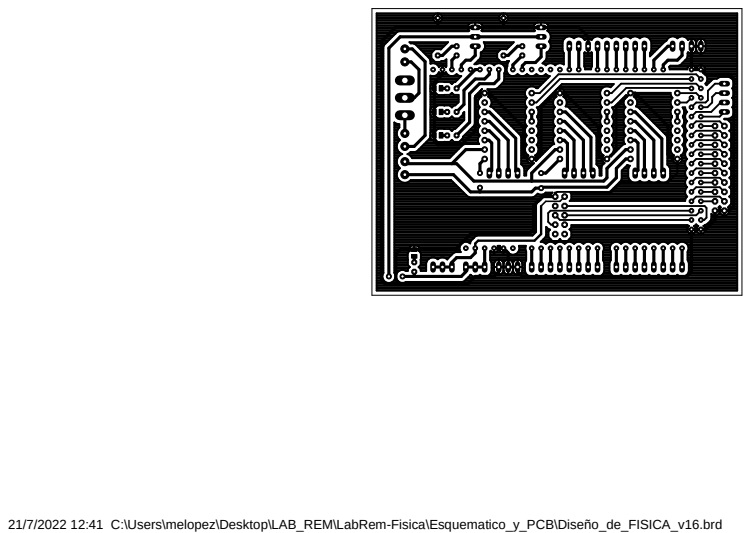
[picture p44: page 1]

21/7/2022 12:41 C:\Users\melopez\Desktop\LAB_REM\LabRem-Fisica\Esquematico_y_PCB\Diseño_de_FISICA_v16.brd

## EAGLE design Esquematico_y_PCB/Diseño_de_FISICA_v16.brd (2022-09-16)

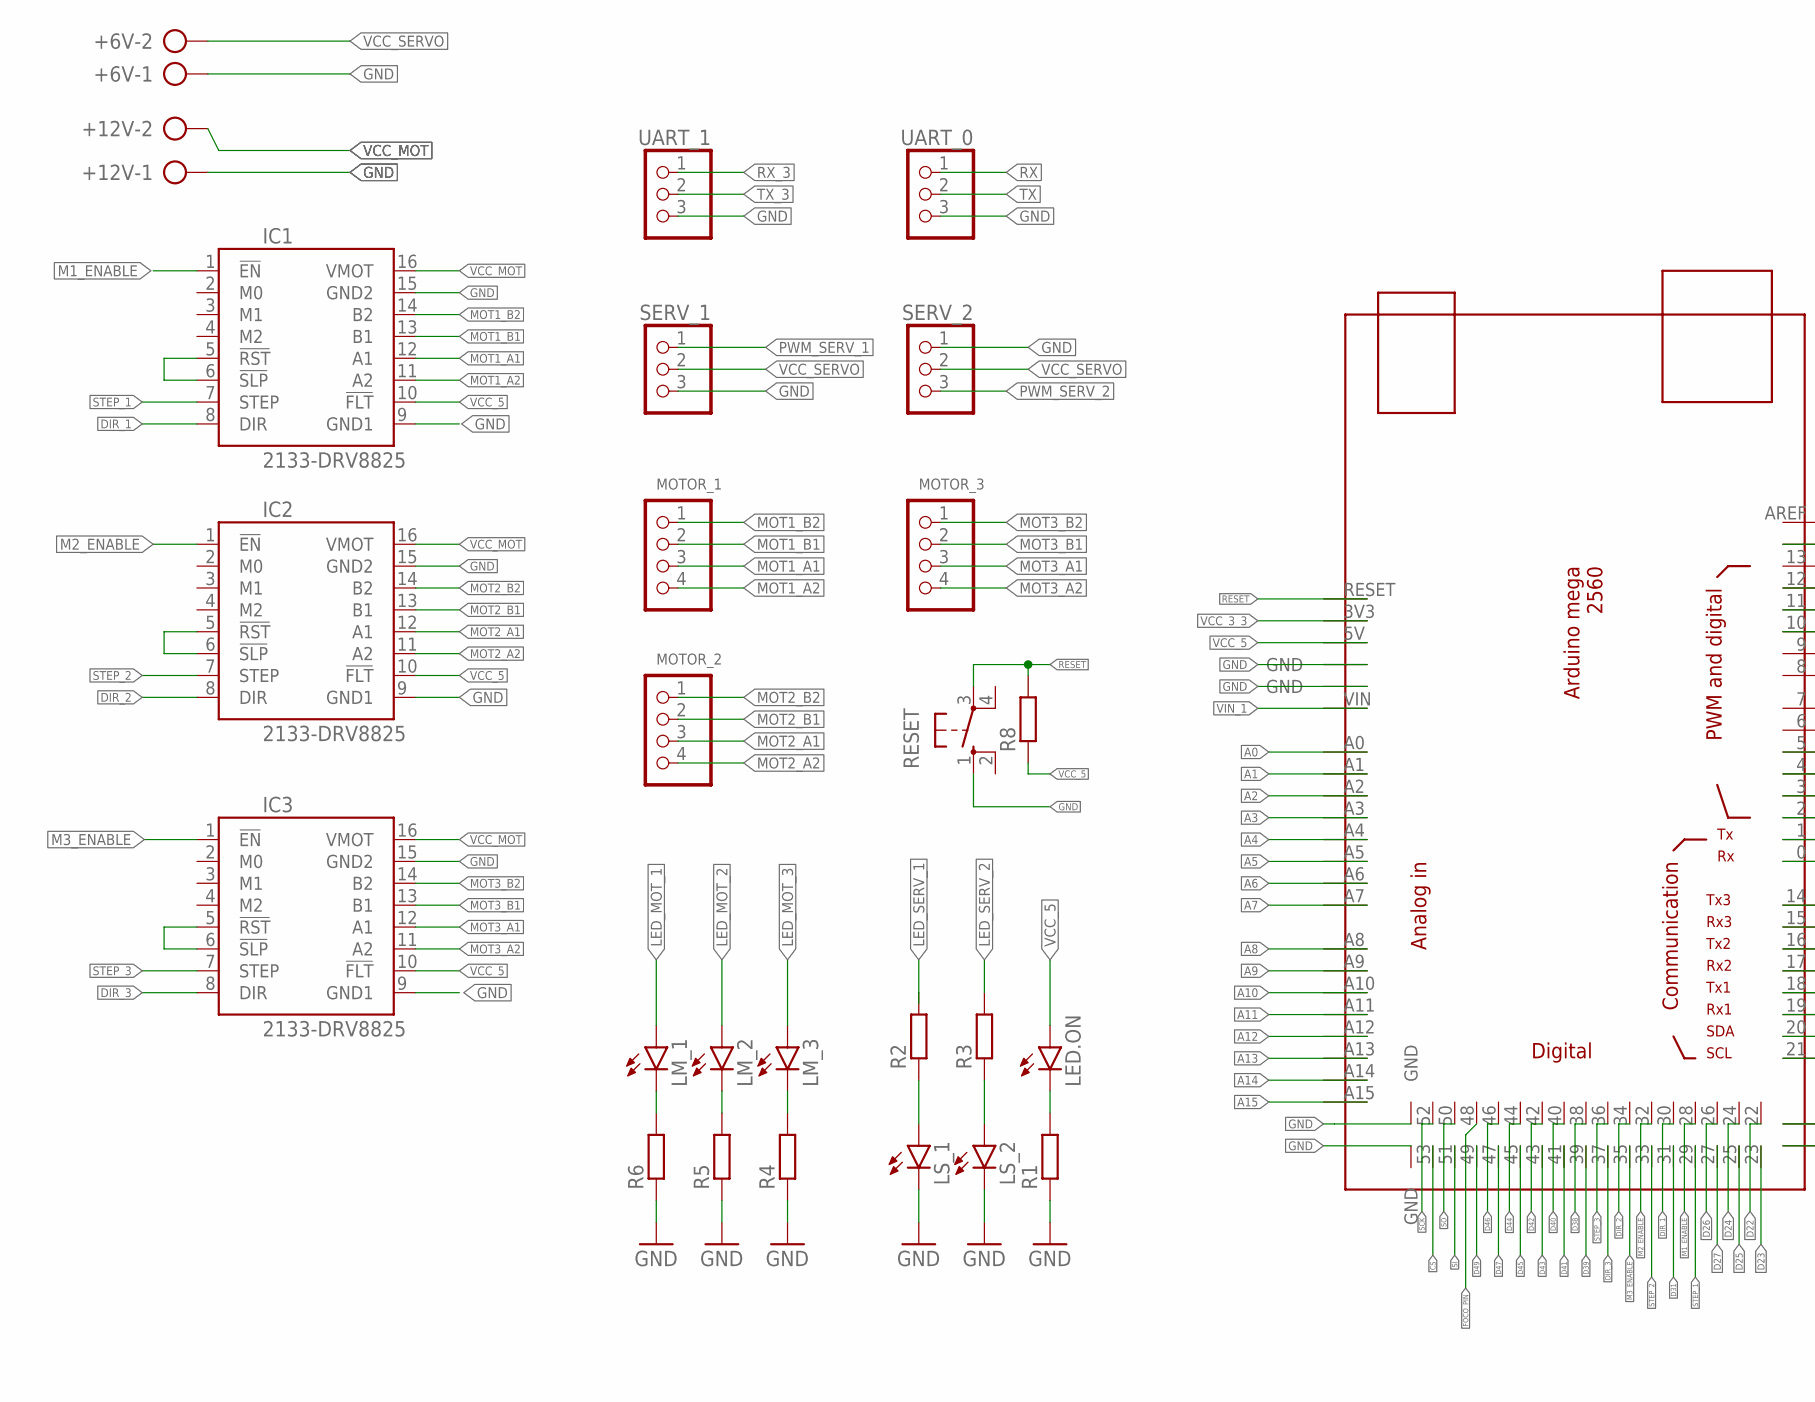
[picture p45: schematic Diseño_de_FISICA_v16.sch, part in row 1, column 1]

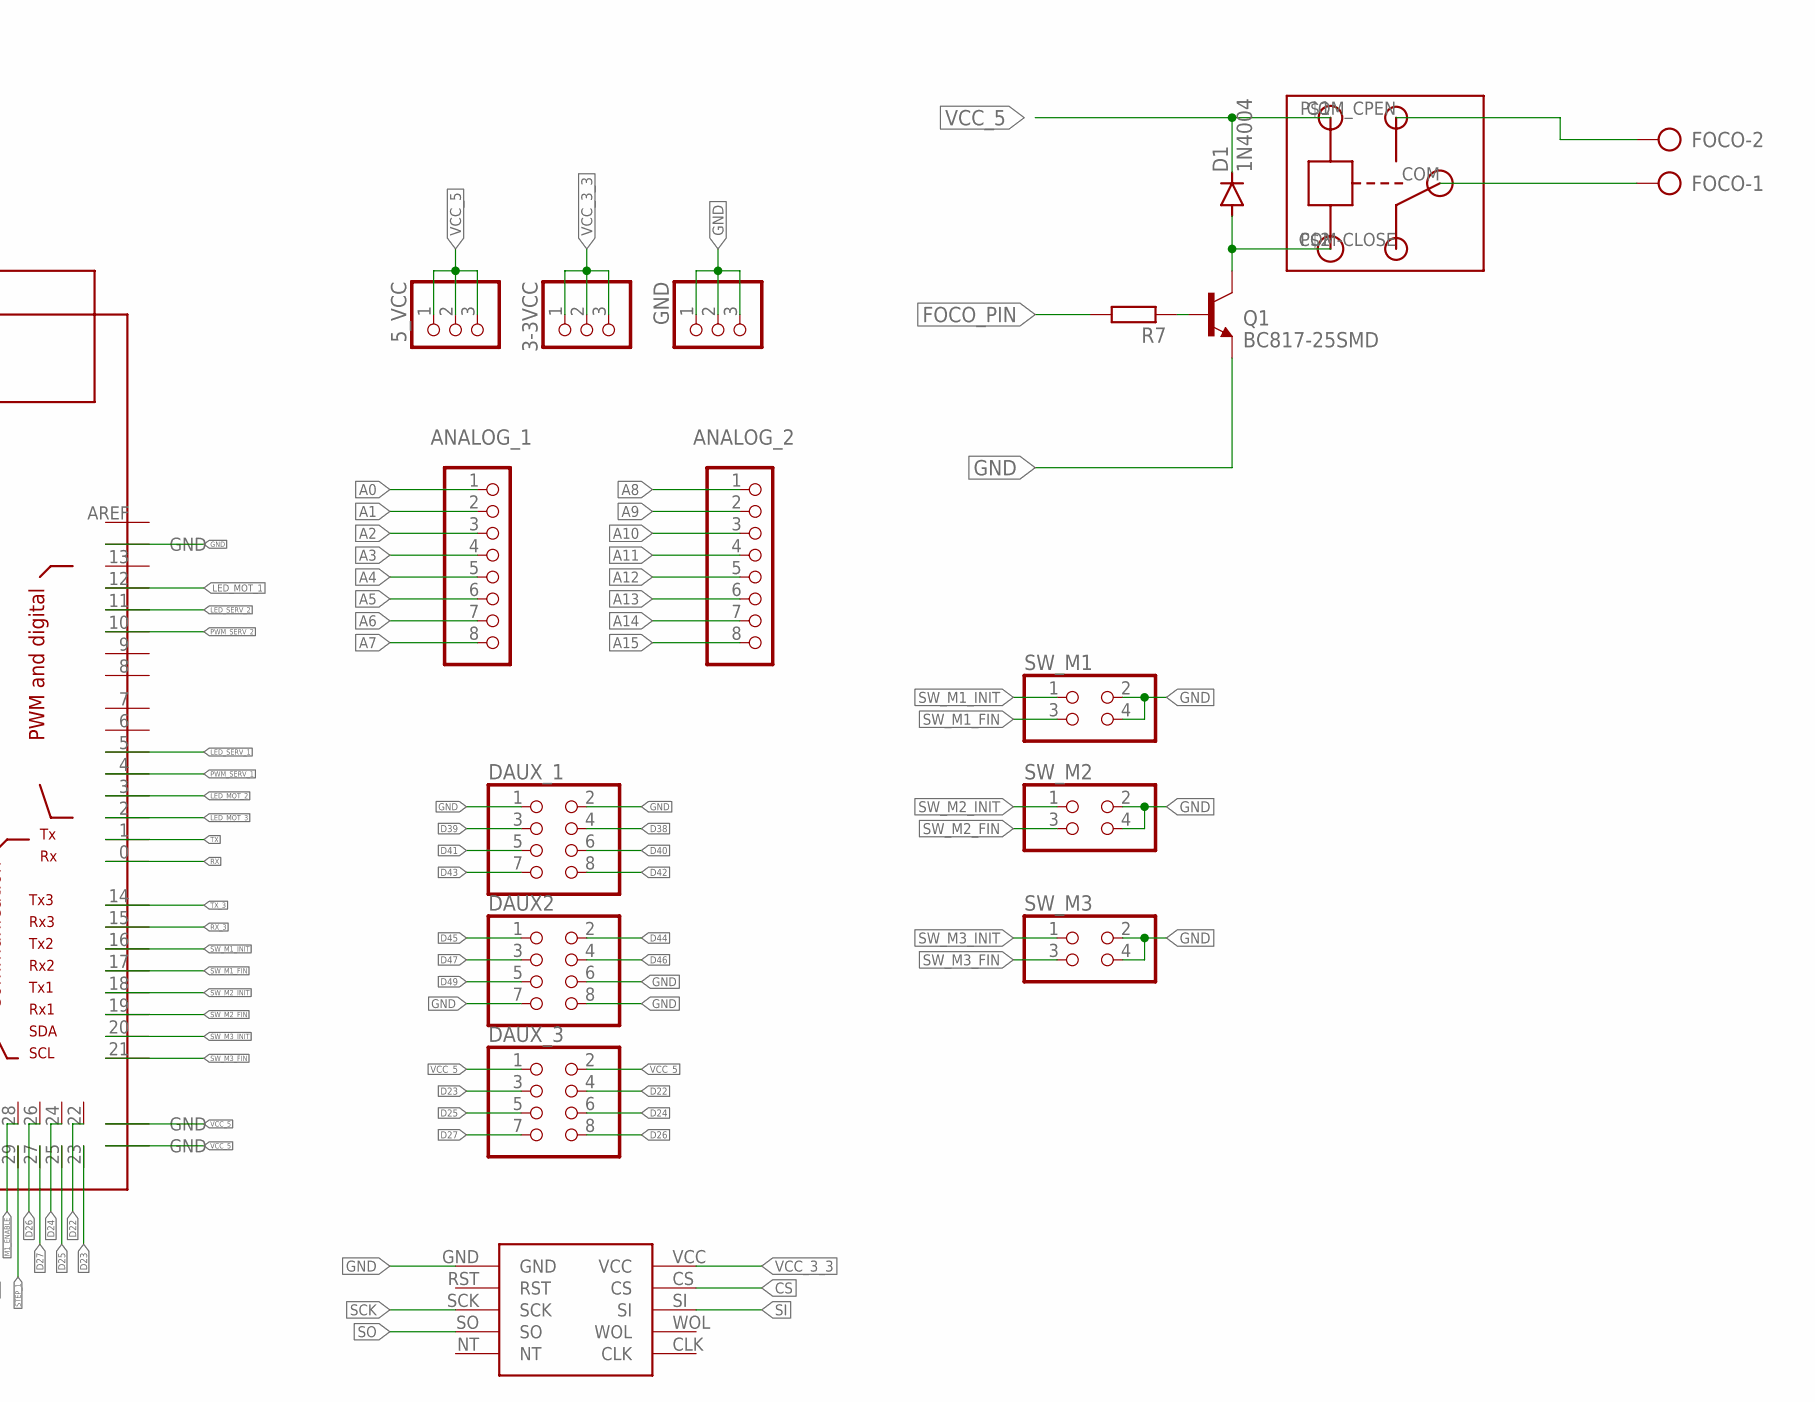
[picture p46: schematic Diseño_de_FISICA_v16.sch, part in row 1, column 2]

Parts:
3-3VCC, 5_VCC: PINHD-1X3; 1X03
+6V, +12V: AK300/2
ANALOG_1, ANALOG_2: PINHD-1X8; 1X08
ARDUINOMEGA2560: MEGA_DEVICE; MEGAOUTLINE
D1: 1N4004; DO41-10
DAUX2: PINHD-2X4; 2X04
DAUX_1, DAUX_3: PINHD-2X4; 2X04
FOCO: AK300/2
GND: PINHD-1X3; 1X03
IC1, IC2, IC3: 2133-DRV8825; DRV8825
LED.ON: LED3MM
LM_1, LM_2, LM_3: LED3MM
LS_1, LS_2: LED3MM
MODULO_ETHERNET: ENC28J60
MOTOR_1, MOTOR_2, MOTOR_3: PINHD-1X4; 1X04
Q1: BC817-25SMD; SOT23-BEC
R1, R2, R3, R4, R5, R6, R7, R8: R_CHIP-0805(2012-METRIC); RESC2012X65
RESET: 10-XX; B3F-10XX
SERV_1, SERV_2: PINHD-1X3; 1X03
SW_M1, SW_M2, SW_M3: PINHD-2X2; 2X02
U$1: RELAY
UART_0, UART_1: PINHD-1X3; 1X03

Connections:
A0: ANALOG_1.1, ARDUINOMEGA2560.A0
A1: ANALOG_1.2, ARDUINOMEGA2560.A1
A2: ANALOG_1.3, ARDUINOMEGA2560.A2
A3: ANALOG_1.4, ARDUINOMEGA2560.A3
A4: ANALOG_1.5, ARDUINOMEGA2560.A4
A5: ANALOG_1.6, ARDUINOMEGA2560.A5
A6: ANALOG_1.7, ARDUINOMEGA2560.A6
A7: ANALOG_1.8, ARDUINOMEGA2560.A7
A8: ANALOG_2.1, ARDUINOMEGA2560.A8
A9: ANALOG_2.2, ARDUINOMEGA2560.A9
A10: ANALOG_2.3, ARDUINOMEGA2560.A10
A11: ANALOG_2.4, ARDUINOMEGA2560.A11
A12: ANALOG_2.5, ARDUINOMEGA2560.A12
A13: ANALOG_2.6, ARDUINOMEGA2560.A13
A14: ANALOG_2.7, ARDUINOMEGA2560.A14
A15: ANALOG_2.8, ARDUINOMEGA2560.A15
CS: ARDUINOMEGA2560.53, MODULO_ETHERNET.CS
D22: ARDUINOMEGA2560.22, DAUX_3.4
D23: ARDUINOMEGA2560.23, DAUX_3.3
D24: ARDUINOMEGA2560.24, DAUX_3.6
D25: ARDUINOMEGA2560.25, DAUX_3.5
D26: ARDUINOMEGA2560.26, DAUX_3.8
D27: ARDUINOMEGA2560.27, DAUX_3.7
D31: ARDUINOMEGA2560.31
D38: ARDUINOMEGA2560.38, DAUX_1.4
D39: ARDUINOMEGA2560.39, DAUX_1.3
D40: ARDUINOMEGA2560.40, DAUX_1.6
D41: ARDUINOMEGA2560.41, DAUX_1.5
D42: ARDUINOMEGA2560.42, DAUX_1.8
D43: ARDUINOMEGA2560.43, DAUX_1.7
D44: ARDUINOMEGA2560.44, DAUX2.2
D45: ARDUINOMEGA2560.45, DAUX2.1
D46: ARDUINOMEGA2560.46, DAUX2.4
D47: ARDUINOMEGA2560.47, DAUX2.3
D49: ARDUINOMEGA2560.49, DAUX2.5
DIR_1: ARDUINOMEGA2560.30, IC1.8 (DIR)
DIR_2: ARDUINOMEGA2560.34, IC2.8 (DIR)
DIR_3: ARDUINOMEGA2560.37, IC3.8 (DIR)
FOCO_PIN: ARDUINOMEGA2560.48, R7.2
GND: +6V.1, +12V.1, ARDUINOMEGA2560.GND@1 (GND), ARDUINOMEGA2560.GND@2 (GND), ARDUINOMEGA2560.GND@3 (GND), ARDUINOMEGA2560.GND@6 (GND), ARDUINOMEGA2560.GND@7 (GND), DAUX2.6, DAUX2.7, DAUX2.8, DAUX_1.1, DAUX_1.2, GND.1, GND.2, GND.3, IC1.9 (GND1), IC1.15 (GND2), IC2.9 (GND1), IC2.15 (GND2), IC3.9 (GND1), IC3.15 (GND2), LS_1.K (C), LS_2.K (C), MODULO_ETHERNET.GND, Q1.E, R1.1, R4.1, R5.1, R6.1, RESET.1 (S), SERV_1.3, SERV_2.1, SW_M1.2, SW_M1.4, SW_M2.2, SW_M2.4, SW_M3.2, SW_M3.4, UART_0.3, UART_1.3
LED_MOT_1: ARDUINOMEGA2560.12, LM_1.A
LED_MOT_2: ARDUINOMEGA2560.3, LM_2.A
LED_MOT_3: ARDUINOMEGA2560.2, LM_3.A
LED_SERV_1: ARDUINOMEGA2560.5, R2.2
LED_SERV_2: ARDUINOMEGA2560.11, R3.2
M1_ENABLE: ARDUINOMEGA2560.28, IC1.1 (!EN)
M2_ENABLE: ARDUINOMEGA2560.32, IC2.1 (!EN)
M3_ENABLE: ARDUINOMEGA2560.35, IC3.1 (!EN)
MOT1_A1: IC1.12 (A1), MOTOR_1.3
MOT1_A2: IC1.11 (A2), MOTOR_1.4
MOT1_B1: IC1.13 (B1), MOTOR_1.2
MOT1_B2: IC1.14 (B2), MOTOR_1.1
MOT2_A1: IC2.12 (A1), MOTOR_2.3
MOT2_A2: IC2.11 (A2), MOTOR_2.4
MOT2_B1: IC2.13 (B1), MOTOR_2.2
MOT2_B2: IC2.14 (B2), MOTOR_2.1
MOT3_A1: IC3.12 (A1), MOTOR_3.3
MOT3_A2: IC3.11 (A2), MOTOR_3.4
MOT3_B1: IC3.13 (B1), MOTOR_3.2
MOT3_B2: IC3.14 (B2), MOTOR_3.1
unnamed: FOCO.2, U$1.COM_CPEN (COM-OPEN)
unnamed: D1.A, Q1.C, U$1.P$2 (GND)
unnamed: FOCO.1, U$1.COM
unnamed: Q1.B, R7.1
unnamed: LS_1.A, R2.1
unnamed: LS_2.A, R3.1
unnamed: IC2.5 (!RST), IC2.6 (!SLP)
unnamed: IC1.5 (!RST), IC1.6 (!SLP)
unnamed: IC3.5 (!RST), IC3.6 (!SLP)
unnamed: LED.ON.K (C), R1.2
unnamed: LM_3.K (C), R4.2
unnamed: LM_2.K (C), R5.2
unnamed: LM_1.K (C), R6.2
PWM_SERV_1: ARDUINOMEGA2560.4, SERV_1.1
PWM_SERV_2: ARDUINOMEGA2560.10, SERV_2.3
RESET: ARDUINOMEGA2560.RESET, R8.2, RESET.3
RX: ARDUINOMEGA2560.0, UART_0.1
RX_3: ARDUINOMEGA2560.15, UART_1.1
SCK: ARDUINOMEGA2560.52, MODULO_ETHERNET.SCK
SI: ARDUINOMEGA2560.51, MODULO_ETHERNET.SI
SO: ARDUINOMEGA2560.50, MODULO_ETHERNET.SO
STEP_1: ARDUINOMEGA2560.29, IC1.7 (STEP)
STEP_2: ARDUINOMEGA2560.33, IC2.7 (STEP)
STEP_3: ARDUINOMEGA2560.36, IC3.7 (STEP)
SW_M1_FIN: ARDUINOMEGA2560.17, SW_M1.3
SW_M1_INIT: ARDUINOMEGA2560.16, SW_M1.1
SW_M2_FIN: ARDUINOMEGA2560.19, SW_M2.3
SW_M2_INIT: ARDUINOMEGA2560.18, SW_M2.1
SW_M3_FIN: ARDUINOMEGA2560.21, SW_M3.3
SW_M3_INIT: ARDUINOMEGA2560.20, SW_M3.1
TX: ARDUINOMEGA2560.1, UART_0.2
TX_3: ARDUINOMEGA2560.14, UART_1.2
VCC_3_3: 3-3VCC.1, 3-3VCC.2, 3-3VCC.3, ARDUINOMEGA2560.3V3, MODULO_ETHERNET.VCC
VCC_5: 5_VCC.1, 5_VCC.2, 5_VCC.3, ARDUINOMEGA2560.5V, ARDUINOMEGA2560.GND@4 (GND), ARDUINOMEGA2560.GND@5 (GND), D1.C, DAUX_3.1, DAUX_3.2, IC1.10 (!FLT), IC2.10 (!FLT), IC3.10 (!FLT), LED.ON.A, R8.1, U$1.P$1 (IN)
VCC_MOT: +12V.2, IC1.16 (VMOT), IC2.16 (VMOT), IC3.16 (VMOT)
VCC_SERVO: +6V.2, SERV_1.2, SERV_2.2
VIN_1: ARDUINOMEGA2560.VIN

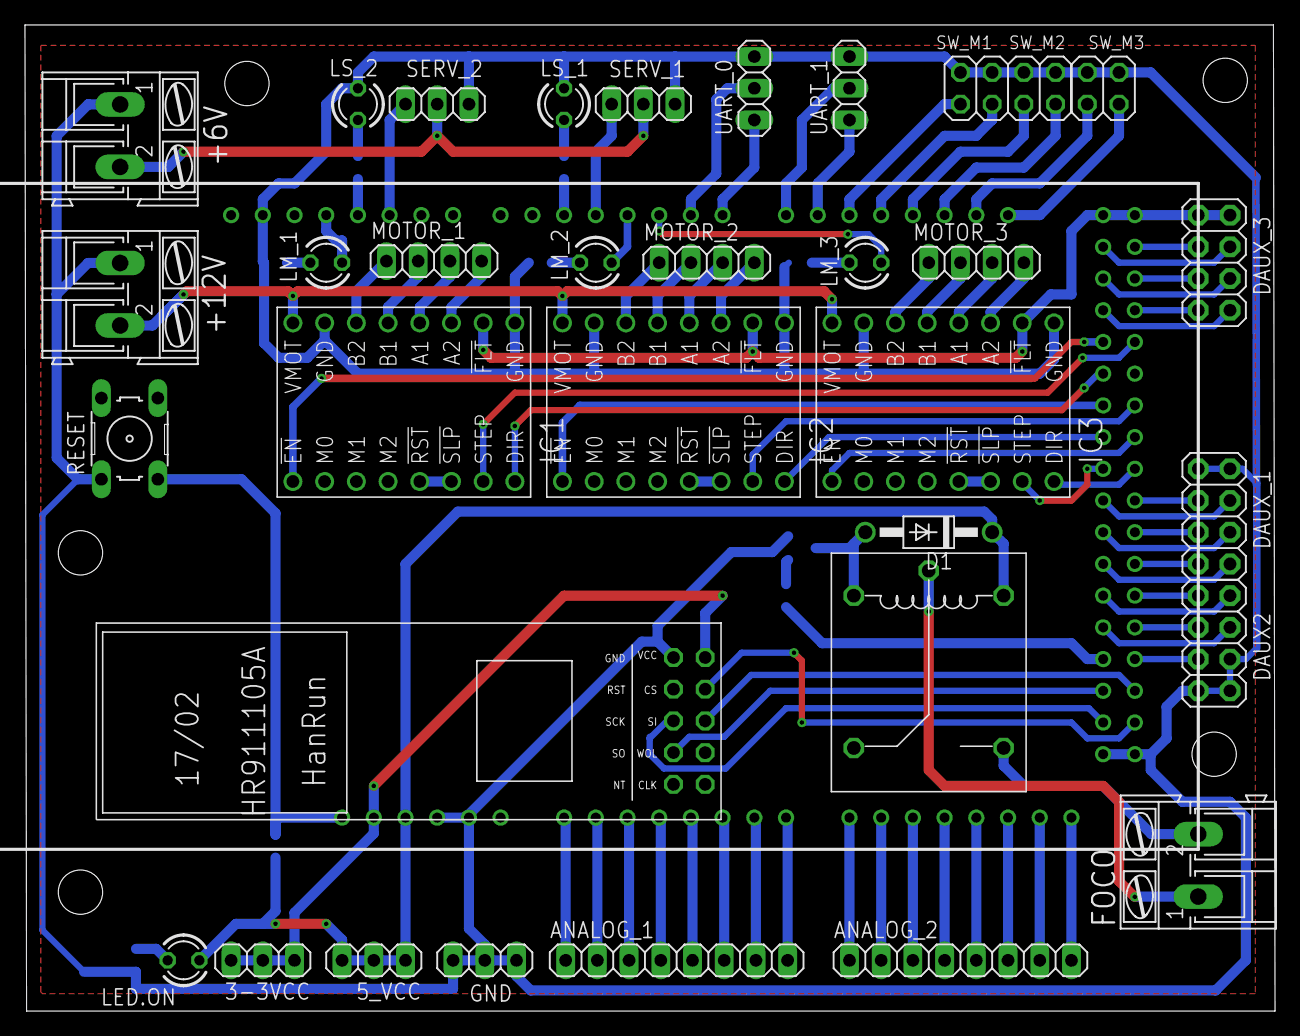
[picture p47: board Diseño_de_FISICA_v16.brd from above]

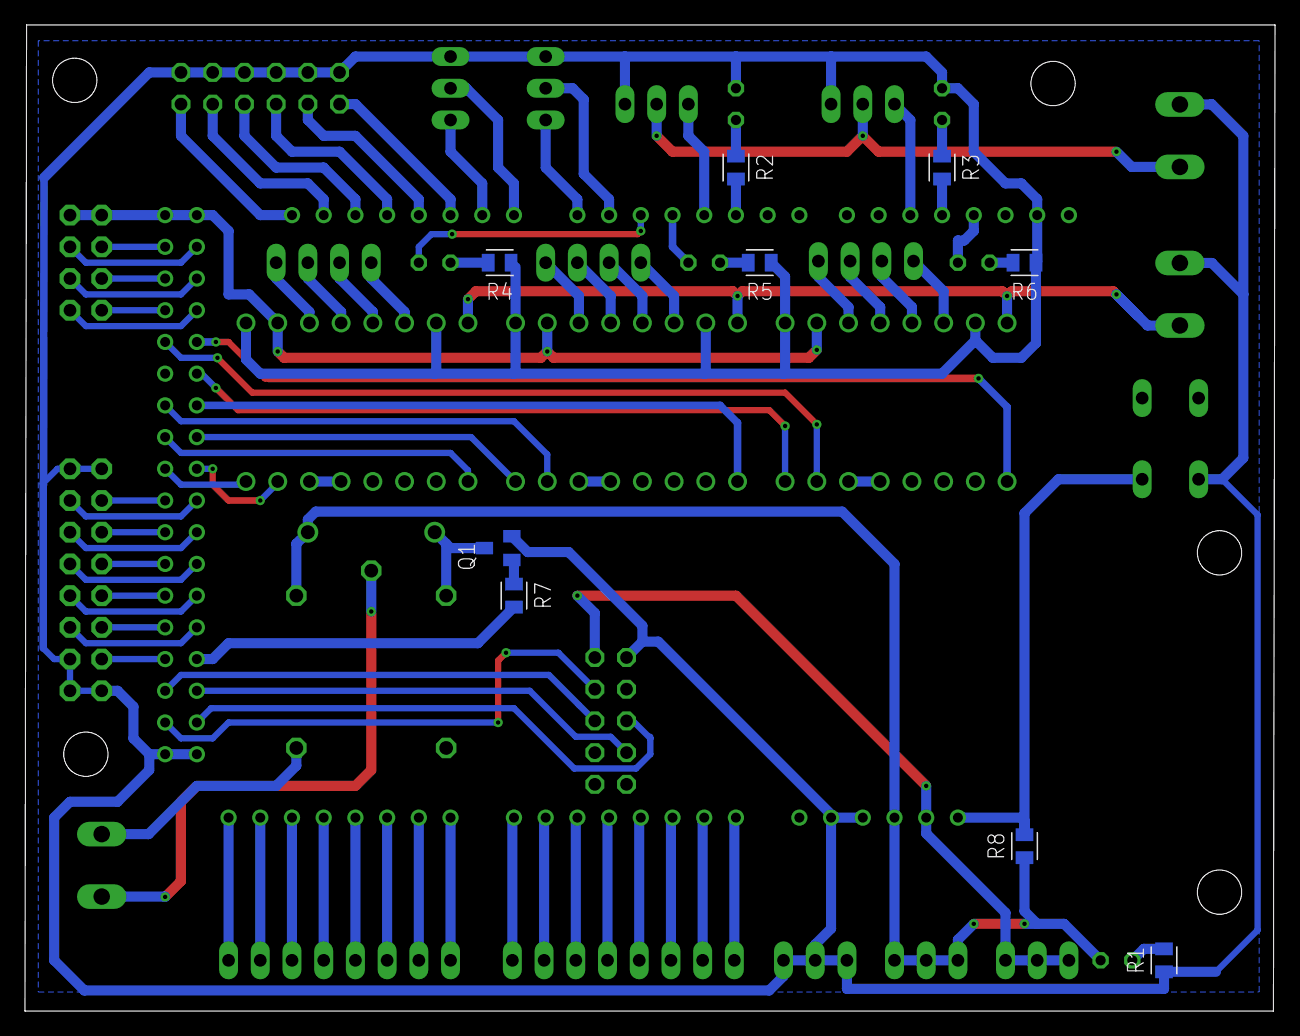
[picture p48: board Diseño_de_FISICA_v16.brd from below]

Board: 2 copper layers, 100.1 x 79.0 mm, 44 parts (9 on the bottom side), 95 nets.

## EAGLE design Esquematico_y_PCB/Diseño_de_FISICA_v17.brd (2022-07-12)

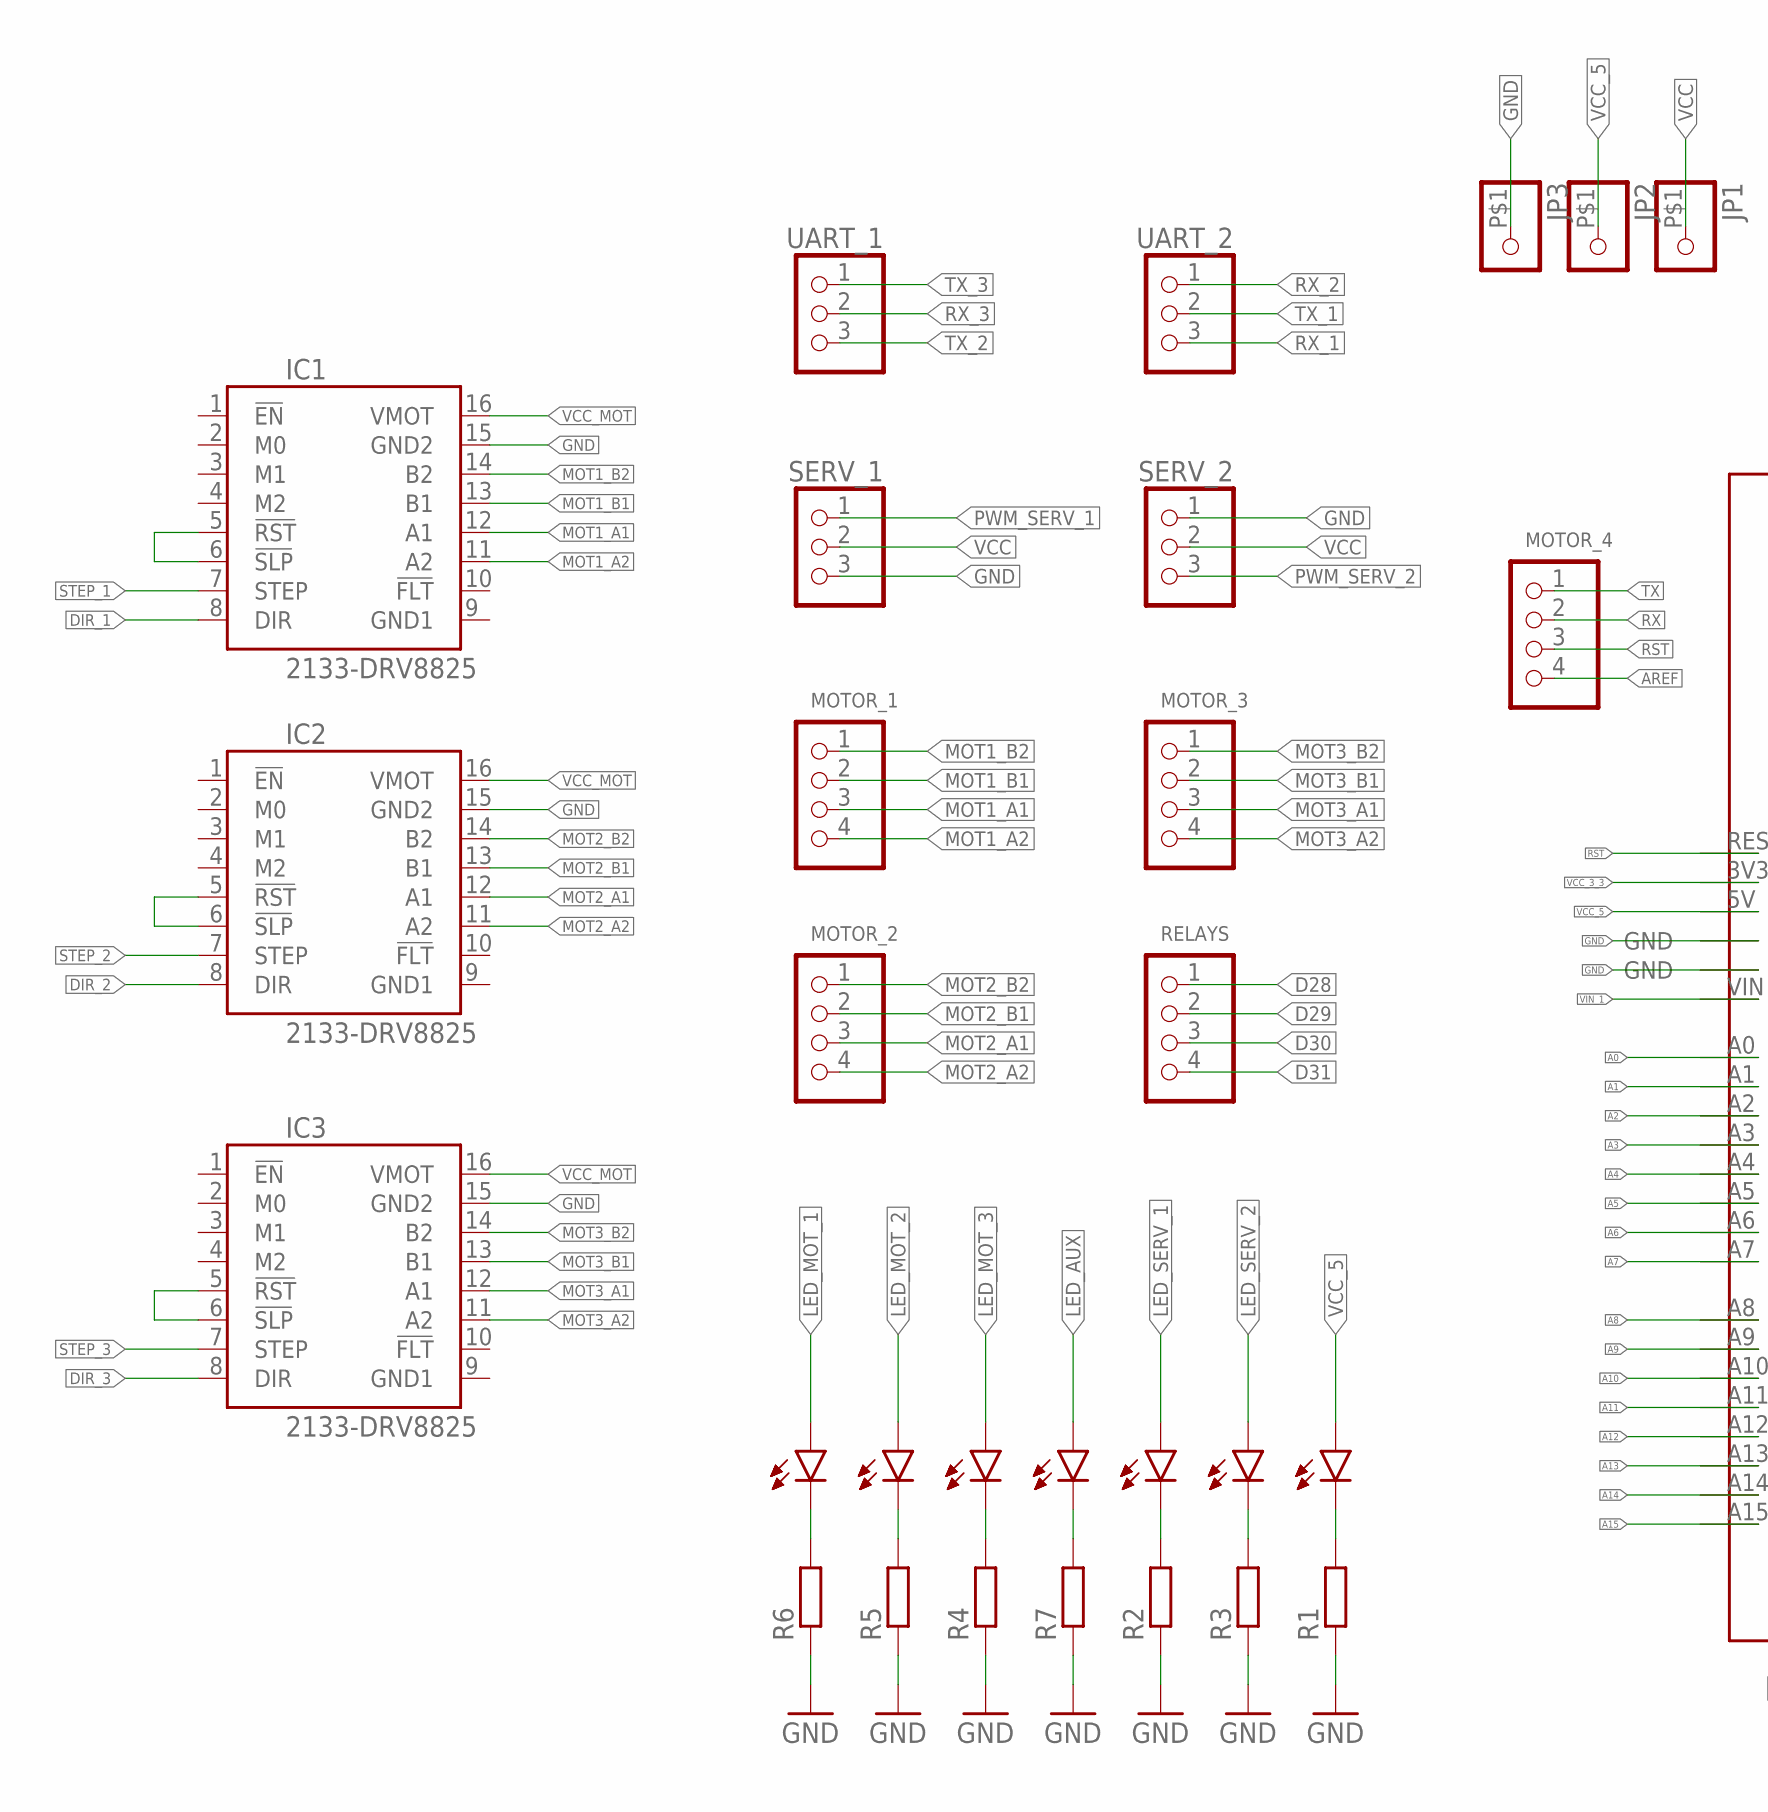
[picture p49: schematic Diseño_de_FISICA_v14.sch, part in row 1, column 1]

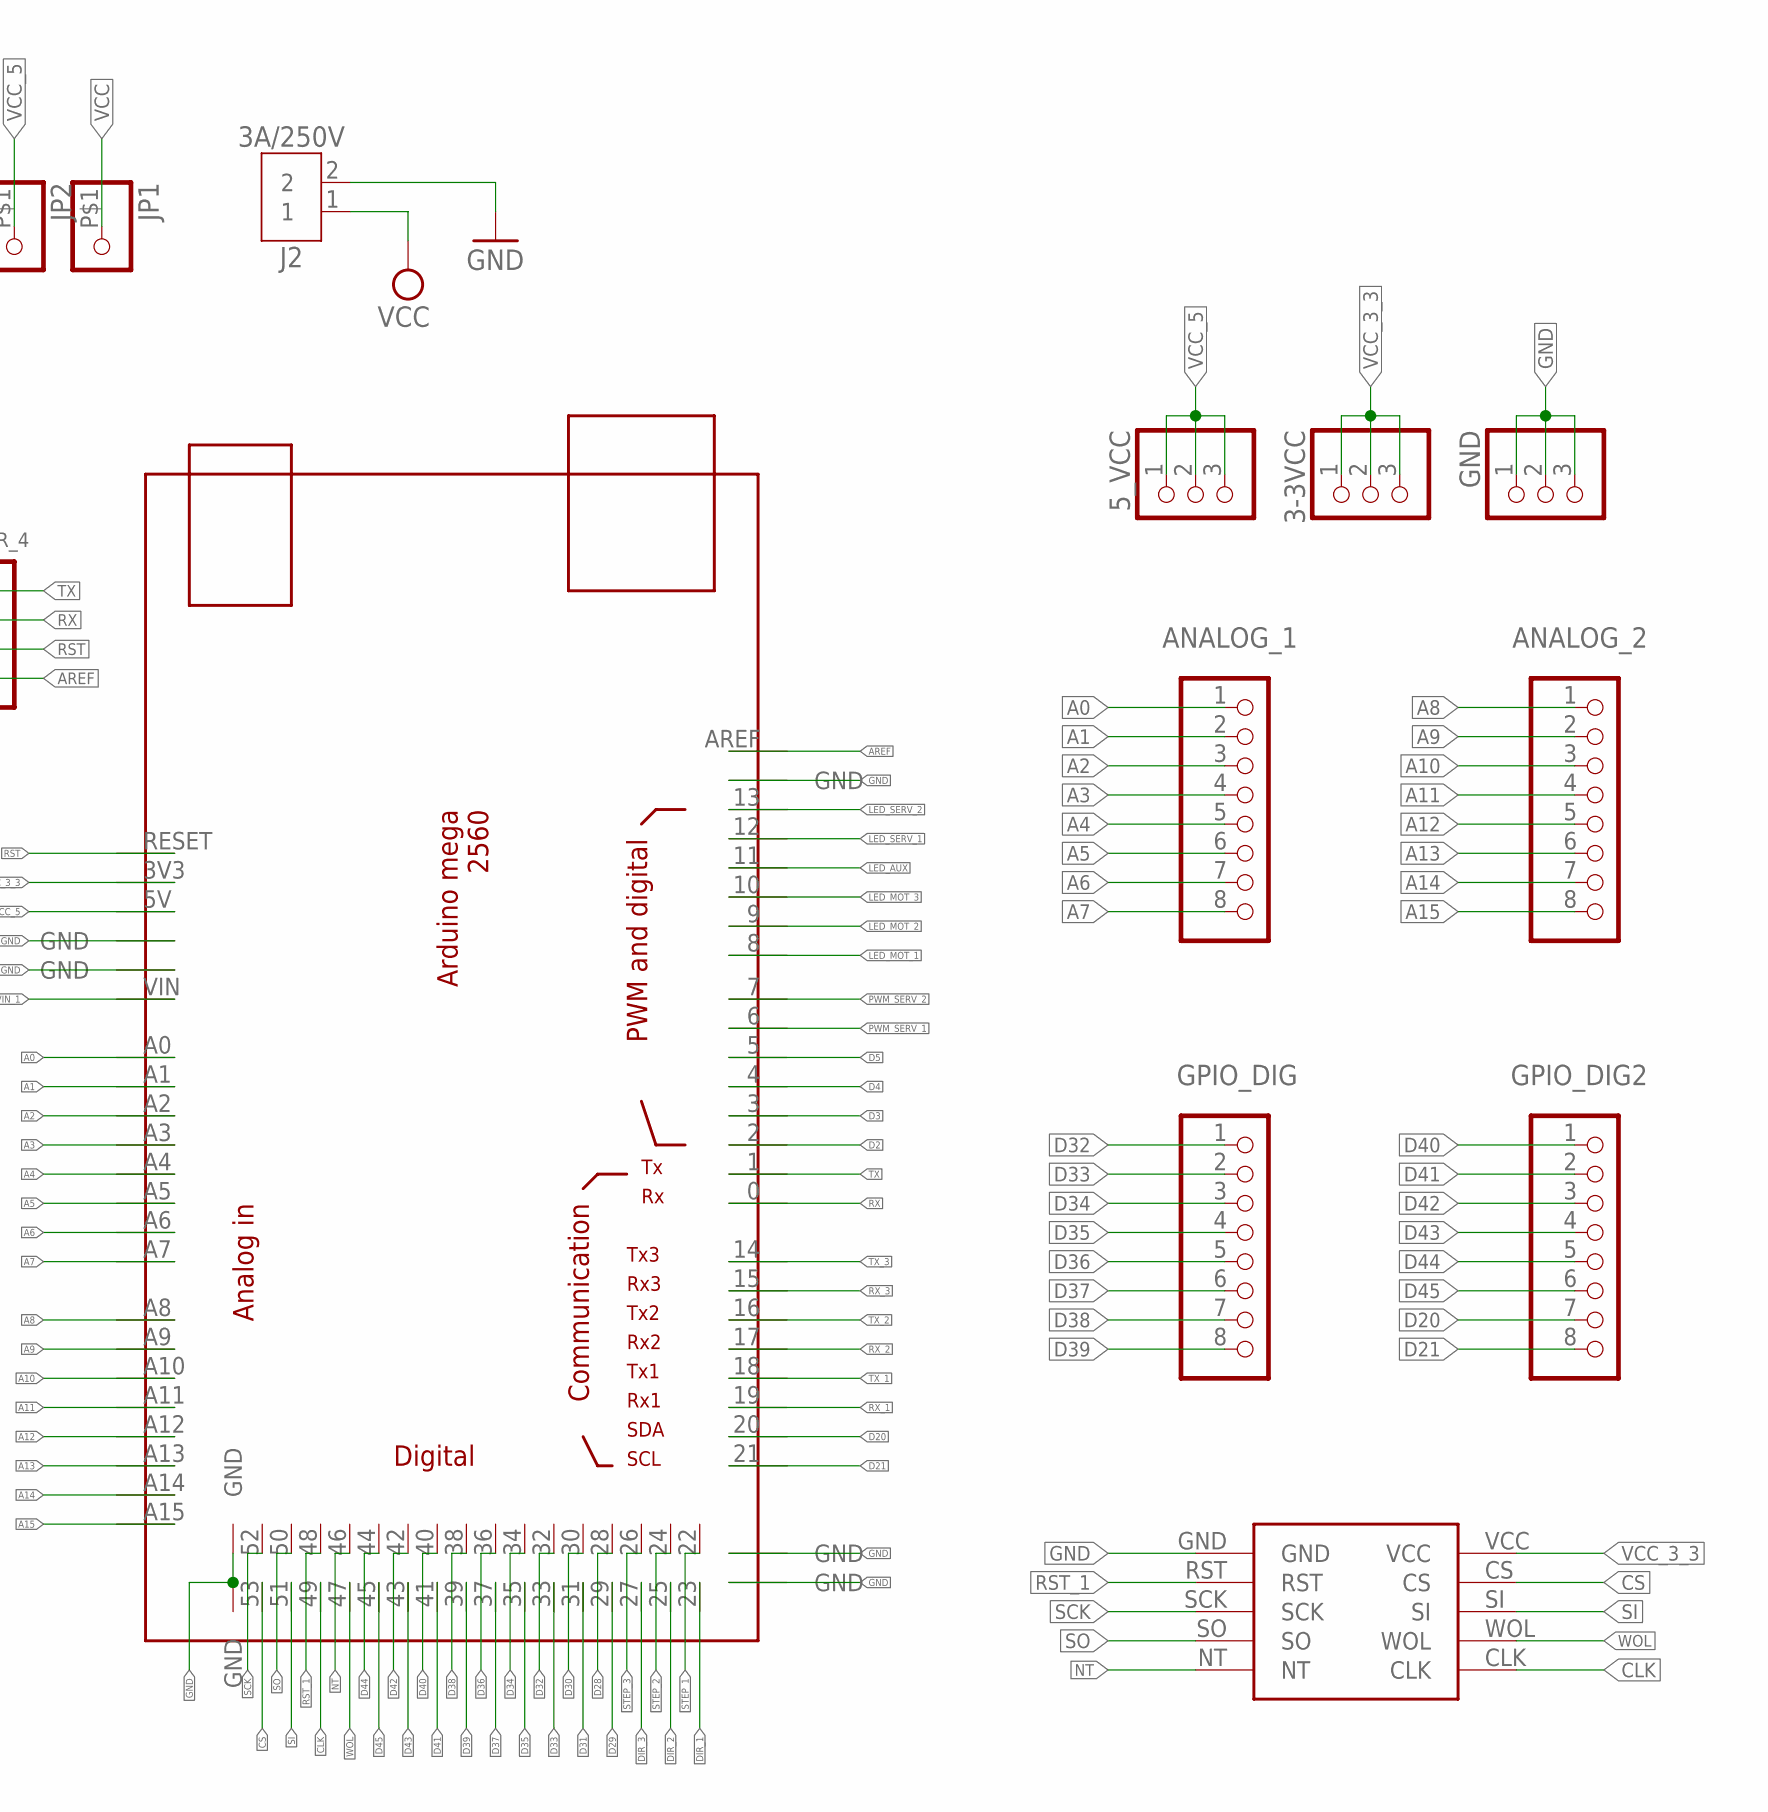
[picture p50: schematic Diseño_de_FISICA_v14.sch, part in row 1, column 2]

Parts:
3-3VCC, 5_VCC: PINHD-1X3; 1X03
ANALOG_1, ANALOG_2: PINHD-1X8; 1X08
ARDUINOMEGA2560: MEGA_DEVICE; MEGAOUTLINE
GND: PINHD-1X3; 1X03
GPIO_DIG, GPIO_DIG2: PINHD-1X8; 1X08
IC1, IC2, IC3: 2133-DRV8825; DRV8825
J2: 3A/250V; B2B-XH-A
JP1, JP2, JP3: PINHD-1X1-BIGPOGO; 1X1-BIGPOGO
LED_AUX: LED_RED; LEDRD254W60D565H860B
LED_MOT1, LED_MOT2, LED_MOT3: LED_RED; LEDRD254W60D565H860B
LED_ON: LED_RED; LEDRD254W60D565H860B
LED_SERV1, LED_SERV2: LED_RED; LEDRD254W60D565H860B
MODULO_ETHERNET: ENC28J60
MOTOR_1, MOTOR_2, MOTOR_3, MOTOR_4: PINHD-1X4; 1X04
R1, R2, R3, R4, R5, R6, R7: R_CHIP-0805(2012-METRIC); RESC2012X65
RELAYS: PINHD-1X4; 1X04
SERV_1, SERV_2: PINHD-1X3; 1X03
UART_1, UART_2: PINHD-1X3; 1X03

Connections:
A0: ANALOG_1.1, ARDUINOMEGA2560.A0
A1: ANALOG_1.2, ARDUINOMEGA2560.A1
A2: ANALOG_1.3, ARDUINOMEGA2560.A2
A3: ANALOG_1.4, ARDUINOMEGA2560.A3
A4: ANALOG_1.5, ARDUINOMEGA2560.A4
A5: ANALOG_1.6, ARDUINOMEGA2560.A5
A6: ANALOG_1.7, ARDUINOMEGA2560.A6
A7: ANALOG_1.8, ARDUINOMEGA2560.A7
A8: ANALOG_2.1, ARDUINOMEGA2560.A8
A9: ANALOG_2.2, ARDUINOMEGA2560.A9
A10: ANALOG_2.3, ARDUINOMEGA2560.A10
A11: ANALOG_2.4, ARDUINOMEGA2560.A11
A12: ANALOG_2.5, ARDUINOMEGA2560.A12
A13: ANALOG_2.6, ARDUINOMEGA2560.A13
A14: ANALOG_2.7, ARDUINOMEGA2560.A14
A15: ANALOG_2.8, ARDUINOMEGA2560.A15
AREF: ARDUINOMEGA2560.AREF, MOTOR_4.4
CLK: ARDUINOMEGA2560.49, MODULO_ETHERNET.CLK
CS: ARDUINOMEGA2560.53, MODULO_ETHERNET.CS
D2: ARDUINOMEGA2560.2
D3: ARDUINOMEGA2560.3
D4: ARDUINOMEGA2560.4
D5: ARDUINOMEGA2560.5
D20: ARDUINOMEGA2560.20, GPIO_DIG2.7
D21: ARDUINOMEGA2560.21, GPIO_DIG2.8
D28: ARDUINOMEGA2560.28, RELAYS.1
D29: ARDUINOMEGA2560.29, RELAYS.2
D30: ARDUINOMEGA2560.30, RELAYS.3
D31: ARDUINOMEGA2560.31, RELAYS.4
D32: ARDUINOMEGA2560.32, GPIO_DIG.1
D33: ARDUINOMEGA2560.33, GPIO_DIG.2
D34: ARDUINOMEGA2560.34, GPIO_DIG.3
D35: ARDUINOMEGA2560.35, GPIO_DIG.4
D36: ARDUINOMEGA2560.36, GPIO_DIG.5
D37: ARDUINOMEGA2560.37, GPIO_DIG.6
D38: ARDUINOMEGA2560.38, GPIO_DIG.7
D39: ARDUINOMEGA2560.39, GPIO_DIG.8
D40: ARDUINOMEGA2560.40, GPIO_DIG2.1
D41: ARDUINOMEGA2560.41, GPIO_DIG2.2
D42: ARDUINOMEGA2560.42, GPIO_DIG2.3
D43: ARDUINOMEGA2560.43, GPIO_DIG2.4
D44: ARDUINOMEGA2560.44, GPIO_DIG2.5
D45: ARDUINOMEGA2560.45, GPIO_DIG2.6
DIR_1: ARDUINOMEGA2560.23, IC1.8 (DIR)
DIR_2: ARDUINOMEGA2560.25, IC2.8 (DIR)
DIR_3: ARDUINOMEGA2560.27, IC3.8 (DIR)
GND: ARDUINOMEGA2560.GND@1 (GND), ARDUINOMEGA2560.GND@2 (GND), ARDUINOMEGA2560.GND@3 (GND), ARDUINOMEGA2560.GND@4 (GND), ARDUINOMEGA2560.GND@5 (GND), ARDUINOMEGA2560.GND@6 (GND), ARDUINOMEGA2560.GND@7 (GND), GND.1, GND.2, GND.3, IC1.15 (GND2), IC2.15 (GND2), IC3.15 (GND2), J2.2, JP3.P$1, MODULO_ETHERNET.GND, R1.1, R2.1, R3.1, R4.1, R5.1, R6.1, R7.1, SERV_1.3, SERV_2.1
GND1: IC1.9 (GND1), IC2.9 (GND1), IC3.9 (GND1)
LED_AUX: ARDUINOMEGA2560.11, LED_AUX.1 (A)
LED_MOT_1: ARDUINOMEGA2560.8, LED_MOT1.1 (A)
LED_MOT_2: ARDUINOMEGA2560.9, LED_MOT2.1 (A)
LED_MOT_3: ARDUINOMEGA2560.10, LED_MOT3.1 (A)
LED_SERV_1: ARDUINOMEGA2560.12, LED_SERV1.1 (A)
LED_SERV_2: ARDUINOMEGA2560.13, LED_SERV2.1 (A)
MOT1_A1: IC1.12 (A1), MOTOR_1.3
MOT1_A2: IC1.11 (A2), MOTOR_1.4
MOT1_B1: IC1.13 (B1), MOTOR_1.2
MOT1_B2: IC1.14 (B2), MOTOR_1.1
MOT2_A1: IC2.12 (A1), MOTOR_2.3
MOT2_A2: IC2.11 (A2), MOTOR_2.4
MOT2_B1: IC2.13 (B1), MOTOR_2.2
MOT2_B2: IC2.14 (B2), MOTOR_2.1
MOT3_A1: IC3.12 (A1), MOTOR_3.3
MOT3_A2: IC3.11 (A2), MOTOR_3.4
MOT3_B1: IC3.13 (B1), MOTOR_3.2
MOT3_B2: IC3.14 (B2), MOTOR_3.1
unnamed: IC2.5 (!RST), IC2.6 (!SLP)
unnamed: IC1.5 (!RST), IC1.6 (!SLP)
unnamed: IC3.5 (!RST), IC3.6 (!SLP)
unnamed: LED_ON.2 (C), R1.2
unnamed: LED_SERV1.2 (C), R2.2
unnamed: LED_SERV2.2 (C), R3.2
unnamed: LED_MOT3.2 (C), R4.2
unnamed: LED_MOT2.2 (C), R5.2
unnamed: LED_MOT1.2 (C), R6.2
unnamed: LED_AUX.2 (C), R7.2
NT: ARDUINOMEGA2560.46, MODULO_ETHERNET.NT
PWM_SERV_1: ARDUINOMEGA2560.6, SERV_1.1
PWM_SERV_2: ARDUINOMEGA2560.7, SERV_2.3
RST: ARDUINOMEGA2560.RESET, MOTOR_4.3
RST_1: ARDUINOMEGA2560.48, MODULO_ETHERNET.RST
RX: ARDUINOMEGA2560.0, MOTOR_4.2
RX_1: ARDUINOMEGA2560.19, UART_2.3
RX_2: ARDUINOMEGA2560.17, UART_2.1
RX_3: ARDUINOMEGA2560.15, UART_1.2
SCK: ARDUINOMEGA2560.52, MODULO_ETHERNET.SCK
SI: ARDUINOMEGA2560.51, MODULO_ETHERNET.SI
SO: ARDUINOMEGA2560.50, MODULO_ETHERNET.SO
STEP_1: ARDUINOMEGA2560.22, IC1.7 (STEP)
STEP_2: ARDUINOMEGA2560.24, IC2.7 (STEP)
STEP_3: ARDUINOMEGA2560.26, IC3.7 (STEP)
TX: ARDUINOMEGA2560.1, MOTOR_4.1
TX_1: ARDUINOMEGA2560.18, UART_2.2
TX_2: ARDUINOMEGA2560.16, UART_1.3
TX_3: ARDUINOMEGA2560.14, UART_1.1
VCC: J2.1, JP1.P$1, SERV_1.2, SERV_2.2
VCC_3_3: 3-3VCC.1, 3-3VCC.2, 3-3VCC.3, ARDUINOMEGA2560.3V3, MODULO_ETHERNET.VCC
VCC_5: 5_VCC.1, 5_VCC.2, 5_VCC.3, ARDUINOMEGA2560.5V, JP2.P$1, LED_ON.1 (A)
VCC_MOT: IC1.16 (VMOT), IC2.16 (VMOT), IC3.16 (VMOT)
VIN_1: ARDUINOMEGA2560.VIN
WOL: ARDUINOMEGA2560.47, MODULO_ETHERNET.WOL

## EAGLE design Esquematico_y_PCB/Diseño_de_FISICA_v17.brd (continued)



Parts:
3-3VCC, 5_VCC: PINHD-1X3; 1X03
ANALOG_1, ANALOG_2: PINHD-1X8; 1X08
ARDUINOMEGA2560: MEGA_DEVICE; MEGAOUTLINE
GND: PINHD-1X3; 1X03
GPIO_DIG, GPIO_DIG2: PINHD-1X8; 1X08
IC1, IC2, IC3: 2133-DRV8825; DRV8825
J2: 3A/250V; B2B-XH-A
JP1, JP2, JP3: PINHD-1X1-BIGPOGO; 1X1-BIGPOGO
LED_AUX: LED_RED; LEDRD254W60D565H860B
LED_MOT1, LED_MOT2, LED_MOT3: LED_RED; LEDRD254W60D565H860B
LED_ON: LED_RED; LEDRD254W60D565H860B
LED_SERV1, LED_SERV2: LED_RED; LEDRD254W60D565H860B
MODULO_ETHERNET: ENC28J60
MOTOR_1, MOTOR_2, MOTOR_3, MOTOR_4: PINHD-1X4; 1X04
R1, R2, R3, R4, R5, R6, R7: R_CHIP-0805(2012-METRIC); RESC2012X65
RELAYS: PINHD-1X4; 1X04
SERV_1, SERV_2: PINHD-1X3; 1X03
UART_1, UART_2: PINHD-1X3; 1X03

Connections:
A0: ANALOG_1.1, ARDUINOMEGA2560.A0
A1: ANALOG_1.2, ARDUINOMEGA2560.A1
A2: ANALOG_1.3, ARDUINOMEGA2560.A2
A3: ANALOG_1.4, ARDUINOMEGA2560.A3
A4: ANALOG_1.5, ARDUINOMEGA2560.A4
A5: ANALOG_1.6, ARDUINOMEGA2560.A5
A6: ANALOG_1.7, ARDUINOMEGA2560.A6
A7: ANALOG_1.8, ARDUINOMEGA2560.A7
A8: ANALOG_2.1, ARDUINOMEGA2560.A8
A9: ANALOG_2.2, ARDUINOMEGA2560.A9
A10: ANALOG_2.3, ARDUINOMEGA2560.A10
A11: ANALOG_2.4, ARDUINOMEGA2560.A11
A12: ANALOG_2.5, ARDUINOMEGA2560.A12
A13: ANALOG_2.6, ARDUINOMEGA2560.A13
A14: ANALOG_2.7, ARDUINOMEGA2560.A14
A15: ANALOG_2.8, ARDUINOMEGA2560.A15
AREF: ARDUINOMEGA2560.AREF, MOTOR_4.4
CLK: ARDUINOMEGA2560.49, MODULO_ETHERNET.CLK
CS: ARDUINOMEGA2560.53, MODULO_ETHERNET.CS
D2: ARDUINOMEGA2560.2
D3: ARDUINOMEGA2560.3
D4: ARDUINOMEGA2560.4
D5: ARDUINOMEGA2560.5
D20: ARDUINOMEGA2560.20, GPIO_DIG2.7
D21: ARDUINOMEGA2560.21, GPIO_DIG2.8
D28: ARDUINOMEGA2560.28, RELAYS.1
D29: ARDUINOMEGA2560.29, RELAYS.2
D30: ARDUINOMEGA2560.30, RELAYS.3
D31: ARDUINOMEGA2560.31, RELAYS.4
D32: ARDUINOMEGA2560.32, GPIO_DIG.1
D33: ARDUINOMEGA2560.33, GPIO_DIG.2
D34: ARDUINOMEGA2560.34, GPIO_DIG.3
D35: ARDUINOMEGA2560.35, GPIO_DIG.4
D36: ARDUINOMEGA2560.36, GPIO_DIG.5
D37: ARDUINOMEGA2560.37, GPIO_DIG.6
D38: ARDUINOMEGA2560.38, GPIO_DIG.7
D39: ARDUINOMEGA2560.39, GPIO_DIG.8
D40: ARDUINOMEGA2560.40, GPIO_DIG2.1
D41: ARDUINOMEGA2560.41, GPIO_DIG2.2
D42: ARDUINOMEGA2560.42, GPIO_DIG2.3
D43: ARDUINOMEGA2560.43, GPIO_DIG2.4
D44: ARDUINOMEGA2560.44, GPIO_DIG2.5
D45: ARDUINOMEGA2560.45, GPIO_DIG2.6
DIR_1: ARDUINOMEGA2560.23, IC1.8 (DIR)
DIR_2: ARDUINOMEGA2560.25, IC2.8 (DIR)
DIR_3: ARDUINOMEGA2560.27, IC3.8 (DIR)
GND: ARDUINOMEGA2560.GND@1 (GND), ARDUINOMEGA2560.GND@2 (GND), ARDUINOMEGA2560.GND@3 (GND), ARDUINOMEGA2560.GND@4 (GND), ARDUINOMEGA2560.GND@5 (GND), ARDUINOMEGA2560.GND@6 (GND), ARDUINOMEGA2560.GND@7 (GND), GND.1, GND.2, GND.3, IC1.15 (GND2), IC2.15 (GND2), IC3.15 (GND2), J2.2, JP3.P$1, MODULO_ETHERNET.GND, R1.1, R2.1, R3.1, R4.1, R5.1, R6.1, R7.1, SERV_1.3, SERV_2.1
GND1: IC1.9 (GND1), IC2.9 (GND1), IC3.9 (GND1)
LED_AUX: ARDUINOMEGA2560.11, LED_AUX.1 (A)
LED_MOT_1: ARDUINOMEGA2560.8, LED_MOT1.1 (A)
LED_MOT_2: ARDUINOMEGA2560.9, LED_MOT2.1 (A)
LED_MOT_3: ARDUINOMEGA2560.10, LED_MOT3.1 (A)
LED_SERV_1: ARDUINOMEGA2560.12, LED_SERV1.1 (A)
LED_SERV_2: ARDUINOMEGA2560.13, LED_SERV2.1 (A)
MOT1_A1: IC1.12 (A1), MOTOR_1.3
MOT1_A2: IC1.11 (A2), MOTOR_1.4
MOT1_B1: IC1.13 (B1), MOTOR_1.2
MOT1_B2: IC1.14 (B2), MOTOR_1.1
MOT2_A1: IC2.12 (A1), MOTOR_2.3
MOT2_A2: IC2.11 (A2), MOTOR_2.4
MOT2_B1: IC2.13 (B1), MOTOR_2.2
MOT2_B2: IC2.14 (B2), MOTOR_2.1
MOT3_A1: IC3.12 (A1), MOTOR_3.3
MOT3_A2: IC3.11 (A2), MOTOR_3.4
MOT3_B1: IC3.13 (B1), MOTOR_3.2
MOT3_B2: IC3.14 (B2), MOTOR_3.1
unnamed: IC2.5 (!RST), IC2.6 (!SLP)
unnamed: IC1.5 (!RST), IC1.6 (!SLP)
unnamed: IC3.5 (!RST), IC3.6 (!SLP)
unnamed: LED_ON.2 (C), R1.2
unnamed: LED_SERV1.2 (C), R2.2
unnamed: LED_SERV2.2 (C), R3.2
unnamed: LED_MOT3.2 (C), R4.2
unnamed: LED_MOT2.2 (C), R5.2
unnamed: LED_MOT1.2 (C), R6.2
unnamed: LED_AUX.2 (C), R7.2
NT: ARDUINOMEGA2560.46, MODULO_ETHERNET.NT
PWM_SERV_1: ARDUINOMEGA2560.6, SERV_1.1
PWM_SERV_2: ARDUINOMEGA2560.7, SERV_2.3
RST: ARDUINOMEGA2560.RESET, MOTOR_4.3
RST_1: ARDUINOMEGA2560.48, MODULO_ETHERNET.RST
RX: ARDUINOMEGA2560.0, MOTOR_4.2
RX_1: ARDUINOMEGA2560.19, UART_2.3
RX_2: ARDUINOMEGA2560.17, UART_2.1
RX_3: ARDUINOMEGA2560.15, UART_1.2
SCK: ARDUINOMEGA2560.52, MODULO_ETHERNET.SCK
SI: ARDUINOMEGA2560.51, MODULO_ETHERNET.SI
SO: ARDUINOMEGA2560.50, MODULO_ETHERNET.SO
STEP_1: ARDUINOMEGA2560.22, IC1.7 (STEP)
STEP_2: ARDUINOMEGA2560.24, IC2.7 (STEP)
STEP_3: ARDUINOMEGA2560.26, IC3.7 (STEP)
TX: ARDUINOMEGA2560.1, MOTOR_4.1
TX_1: ARDUINOMEGA2560.18, UART_2.2
TX_2: ARDUINOMEGA2560.16, UART_1.3
TX_3: ARDUINOMEGA2560.14, UART_1.1
VCC: J2.1, JP1.P$1, SERV_1.2, SERV_2.2
VCC_3_3: 3-3VCC.1, 3-3VCC.2, 3-3VCC.3, ARDUINOMEGA2560.3V3, MODULO_ETHERNET.VCC
VCC_5: 5_VCC.1, 5_VCC.2, 5_VCC.3, ARDUINOMEGA2560.5V, JP2.P$1, LED_ON.1 (A)
VCC_MOT: IC1.16 (VMOT), IC2.16 (VMOT), IC3.16 (VMOT)
VIN_1: ARDUINOMEGA2560.VIN
WOL: ARDUINOMEGA2560.47, MODULO_ETHERNET.WOL

Board: 2 copper layers, 39 parts (0 on the bottom side), 96 nets, no tracks yet.

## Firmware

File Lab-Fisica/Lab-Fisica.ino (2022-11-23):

// Defino las librerias a utilizar
#include <ArduinoJson.h> // Para el manejo y conversión de JSON a vartiables
#include <UIPEthernet.h> // Para el manejo del Shield Ethernet
#include <Servo.h> // Para el manejo de los Servos.
//----------------------------------------------//
// Defino el servidor y el Puerto
#define server_port 22 // 80
EthernetServer server = EthernetServer(server_port);
//----------------------------------------------//
// Defino variables para Json
#define const_mje 256
#define const_valores 241
//----------------------------------------------//
//------- Defino mensajes de error predeterminado
// una variable error int
uint8_t Errores = 0;
// 0 - Sin errores
// 1 - Error de distancia.
// 2 - Error de tipo de diafragma.
// 3 - Laboratorio incorrecto.

//----------------------------------------------//
//------- Defino Nombres de pines
//----------------------------------------------//
// MOTORES
//---Leds 
  #define M1_Led 12 // Indicador Motor 1
  #define M2_Led 3// Indicador Motor 2
  #define M3_Led 2 // Indicador Motor 3
//---Finales de carrera
  #define M1_SW_inicio 16 // Motor Foco 1
  #define M1_SW_fin 17    
  #define M2_SW_inicio 18 // Motor Pantalla 2
  #define M2_SW_fin 19
  #define M3_SW_inicio 20 // Motor Lente Div 3
  #define M3_SW_fin 21
//---Control de movimiento
  #define M1_Step 29
  #define M1_Direction 30
  #define M2_Step 33
  #define M2_Direction 34
  #define M3_Step 36
  #define M3_Direction 37
//---Enables
  #define M1_Enable 28
  #define M2_Enable 32
  #define M3_Enable 35
//----------------------------------------------//
//SERVOS
//---Leds 
  #define S_Diafragma_Led 5  // Indicador Servo Diafragma 1
  #define S_Lente_Led 11 // Indicador Servo Lente 2
//---Control de movimiento
  #define S_Diafragma_Pin 4 // Servo diafragma
  #define S_Lente_Pin 10 // Servo lente divergente
// Declaramos la variable para controlar el servo
  Servo servo_diafragma;
  Servo servo_lente;
//----------------------------------------------//
//FOCO - LAMPARA LED 3W
  #define Foco_pin 48 // Pin para habilitar relay de lampara.
//----------------------------------------------//
//Sentidos
  #define AntiHorario HIGH
  #define Horario LOW
// VAriables de json 
// CONSTANTES
#define min_real_fl1 50
#define max_real_fl1 920
//#define min_real_fl2 120
#define max_real_fl2 970
//#define min_real_l2p 70
#define max_real_l2p 970
//#define min_real_l1l2 70
#define max_real_l1l2 900 

//---Estado
  int num_Lab=3; // 0 [Sist Dig], 1 [Sist Control], 2[Telecomunicaciones], 3[Fisica] 
  bool subLab=0; // 1 [SubLab 1], 0 [SubLab 2]
  bool iniLab=0;// 1 [Inicia Experimento], 0 [Finaliza Experimento]
//---Analogico
  int distancia_fl2_act = max_real_fl2; // Distancia actual entre fuente y lente convergente (fija)
  int distancia_fl1_act = max_real_fl1; // Distancia actual entre fuente y lente div
  int distancia_l1l2_act= max_real_l1l2; // Distancia actual entre lente div y lente convergente (fija)
  int distancia_l2p_act=max_real_l2p; // Distancia actual entre lente convergente (fija) y pantalla
  int tipo_diafragma;
//----------------------------------------------//
//--- Variables auxiliares ---//
#define min_mot_l1 50
#define min_mot_p 50
#define min_mot_f 100
#define max_mot_l1 920
#define max_mot_p 950
#define max_mot_f 950
#define dif_real_motor 20
//----------------------------------------------//
// CALCULO DE DISTANCIAS ( Considerar diferencias de distancias generadas por las bases y la separación)
  int distancia_act_foco; //Distancia actual de motor de fuente de luz
  int distancia_act_lente_div; // Distancia actual de motor de lente divergente
  int distancia_act_pantalla; // Distancia actual de motor de pantalla
  int dist_mov; // distancia que se debe mover el motor en realidad. dist_mov=distancia_actual - distancia_deseada
  bool sentido=0; // indica el sentido de giro.
/*
Lente 2 = convergente
Lente 1 = divergente

Distancias reales: 
min_l1l2 = 60 mm -- uso 70 mm Real entre lente 1 y 2
max_l1l2 = 900 mm Real entre lente 1 y 2
min_l2p = 60 mm -- uso 70 mm  Real entre lente 2 y pantalla
max_l2p = 980 mm Real entre lente 2 y pantalla
min_fl1 = 40 mm -- uso 50 mm Real entre fuente y lente 1
max_fl1 = 920 mm Real entre fuente y lente 1
min_fl2 = 100 mm -- uso 120 mm Real entre fuente y lente 2
max_fl2 = 980 mm Real entre fuente y lente 2

Posiciones Motores:
min_l1 = 40 mm -- uso 50 desde el inicio de la barra
max_l1 = 940 mm -- uso 920 desde el inicio de la barra
Desplazamiento max l1= 870 mm
min_p = 40 mm -- uso 50 desde el inicio de la barra
max_p = 960 mm -- uso 950 desde el inicio de la barra
Desplazamiento max p = 900 mm
min_f = 80 mm -- uso 100 desde el inicio de la barra
max_f = 960 mm -- uso 950 desde el inicio de la barra
Desplazamiento max f = 850 mm

Condiciones:
Distancia_fl1 = pos_f - pos_l1 > 50 mm
Distancia_l1l2 = pos_l1 > 50 mm
Distancia_fl2 = pos_f > 120 mm
Distancia_l2p = pos_p > 50 mm 
*/

// BANDERAS
  bool bandera_fin_m1=0; // bandera para determinar fin de mov de motor 1
  bool bandera_fin_m2=0; // bandera para determinar fin de mov de motor 2
  bool bandera_fin_m3=0; // bandera para determinar fin de mov de motor 3
  bool bandera_vueltas=0;// sirve para hacer el conteo de vueltas. Cuando termina se activa.
  bool bandera_rep=0; // bandera para limitar la cantidad de repeticiones de mensaje de lab incorrecto 
  bool bandera_cero=0;    // indica que ya se puso a cero el motor.
// CONTADORES
  int stepDelay = 5; //delay de cada paso del motor
  int conta_pasos=0; // contador de pasos para realizar una vuelta.
//----------------------------------------------//

// Realizo las configuraciones iniciales
void setup() {
  uint8_t myMAC[6] = {0xDE, 0xAD, 0xBE, 0xEF, 0xFE, 0xED}; // defino mac del dispositivo.
  IPAddress myIP(192,168,1,108); // 172.20.5.140 Defino IP Address del dispositivo. 
  Serial.begin(115200); // Inicializo Puerto serial 0 
  while (!Serial) continue; 
  Ethernet.begin(myMAC,myIP);  // Inicializo libreria Ethernet
  server.begin(); // Start to listen
  Serial.println(F("Server is ready."));
  Serial.print(F("Please connect to http://"));
  Serial.println(Ethernet.localIP());
  Serial.println("Port:" + (String)server_port);
// ------- Defino GPIO MODE (INPUT/OUTPUT)--------  //  
// Motor 1
  pinMode(M1_Step, OUTPUT);
  pinMode(M1_Direction, OUTPUT);
  pinMode(M1_Enable, OUTPUT); // Enable Motor 1
  pinMode(M1_SW_inicio,INPUT_PULLUP);
  pinMode(M1_SW_fin,INPUT_PULLUP);
// Motor 2
  pinMode(M2_Step, OUTPUT);
  pinMode(M2_Direction, OUTPUT);
  pinMode(M2_Enable, OUTPUT); // Enable Motor 2
  pinMode(M2_SW_inicio,INPUT_PULLUP);
  pinMode(M2_SW_fin,INPUT_PULLUP);
// Motor 3
  pinMode(M3_Step, OUTPUT);
  pinMode(M3_Direction, OUTPUT);
  pinMode(M3_Enable, OUTPUT); // Enable Motor 3
  pinMode(M3_SW_inicio,INPUT_PULLUP);
  pinMode(M3_SW_fin,INPUT_PULLUP);
  // Leds
  pinMode(M1_Led, OUTPUT); // Led Motor 1
  pinMode(M2_Led, OUTPUT); // Led Motor 2
  pinMode(M3_Led, OUTPUT); // Led Motor 3
  pinMode(S_Diafragma_Led, OUTPUT); // Led Servo 1
  pinMode(S_Lente_Led, OUTPUT); // Led Servo 2
 // Foco (LED)
  pinMode(Foco_pin, OUTPUT);
// Servos
  servo_diafragma.attach(S_Diafragma_Pin);
  servo_lente.attach(S_Lente_Pin);
  //------ Definir estados iniciales ------//
  busco_cero();
}

void loop() {
  //////////// Strings de comunicación /////////////
  char Mensaje_recibido[const_mje] = {0}; // Mensaje recibido por ethernet. (Comando + JSON) 
  char valores_recibidos[const_valores] = {0}; // JSON recibido.  // Wait for an incomming connection
  EthernetClient client = server.available(); 
  if(client){ // Si tengo un cliente conectado
    while (client.available()){ 
      if(bandera_rep==1) {bandera_rep=0;} //reinicio bandera de repetición cuando tengo un mje nuevo.
//      Serial.println("New Command");
      client.readBytesUntil('\r', Mensaje_recibido, sizeof(Mensaje_recibido)); // Tomo el mensaje recibido.
      strncpy(valores_recibidos,&Mensaje_recibido[15],(sizeof(Mensaje_recibido)-15)); 
      Serial.print("Mensaje Recibido"); //      Serial.println(Mensaje_recibido);   //      Serial.print("Json_Recibido: "); //      Serial.println(valores_recibidos);   
      //------ GET ----- //
      if (strstr(Mensaje_recibido, "GET /HTTP/1.1") != NULL) { // Compruebo si llega un GET, respondo valores actuales
        StaticJsonDocument<256> doc;     
        JsonArray Estado = doc.createNestedArray("Estado");
        Estado.add(num_Lab);
        Estado.add(subLab);
        Estado.add(iniLab);
        JsonArray Analogicos = doc.createNestedArray("Analogicos");
        Analogicos.add(tipo_diafragma);
        if(subLab){
          Analogicos.add(distancia_act_foco + dif_real_motor); // distancia del luz a lente fijo
          Analogicos.add(distancia_act_pantalla + dif_real_motor); // distancia lente fijo a pantalla
        }else{
          Analogicos.add(distancia_act_foco - distancia_act_lente_div); 
          Analogicos.add(distancia_act_pantalla + dif_real_motor);
          Analogicos.add(distancia_act_lente_div + dif_real_motor);
        }
        JsonArray Error = doc.createNestedArray("Error");  
        Error.add(Errores);
        Serial.print(F("Sending: "));
        serializeJson(doc, Serial);
        Serial.println();
        client.println(F("HTTP/1.0 200 OK"));   // Write response headers
        client.println(F("Content-Type: application/json"));
        client.print(F("Content-Length: "));  // client.println(F("Connection: close"));
        client.println(measureJsonPretty(doc));
        client.println();
        serializeJsonPretty(doc, client);  // Write JSON document
        client.println(F("Get terminado"));  // Disconnect  //      client.stop();
      }
      //------- POST -----//      
        if (strstr(Mensaje_recibido, "POST /HTTP/1.1") !=NULL) { // Compruebo si llega un POST y respondo, habilito banderas.
        if (bandera_vueltas) {bandera_fin_m1=0; bandera_fin_m2=0; bandera_fin_m3=0; bandera_vueltas=0;}
        Serial.println("Solicitud de escritura recibida");        
        client.println();
        client.println(F("HTTP/1.1 200 OK"));
        client.println();
        StaticJsonDocument<256> doc; // Creo un doc de json
        DeserializationError error = deserializeJson(doc, valores_recibidos); // Deserializo
        if (error){ // Analizo posibles errores.
          Serial.print(F("deserializeJson() failed: "));
          Serial.println(error.f_str());
          return;
        }
        JsonArray Estado = doc["Estado"];
          num_Lab = Estado[0]; // 0 [Sist Dig], 1 [Sist Control], 2[Telecomunicaciones], 3[Fisica]
          subLab = Estado[1]; // 1 [SubLab 1], 0 [SubLab 2]
          iniLab = Estado[2]; // 1 [Inicia Experimento], 0 [Finaliza Experimento]
        if(num_Lab==3){ // Control de numero de lab.
          JsonArray Analogico = doc["Analogico"];
          tipo_diafragma = Analogico[0];
         if(subLab){
            Serial.println("Sub - Laboratorio: Lentes convergentes"); 
            distancia_fl2_act = Analogico[1];
            distancia_fl2_act = distancia_fl2_act - dif_real_motor;
            distancia_l2p_act = Analogico[2];
            distancia_l2p_act = distancia_l2p_act - dif_real_motor;
          }else{
            Serial.println("Sub - Laboratorio: Lentes Divergentes");  
            distancia_fl1_act = Analogico[1];
            distancia_fl1_act = distancia_fl1_act - dif_real_motor;
            distancia_l2p_act = Analogico[2];
            distancia_l2p_act = distancia_l2p_act - dif_real_motor;
            distancia_l1l2_act = Analogico[3];
            distancia_l1l2_act = distancia_l1l2_act - dif_real_motor;
          } 
        }
      }
    }
  }
  else{ // Si no está el cliente enviando algo, sigo haciendo lo que corresponde.
    Control();
  }
}
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

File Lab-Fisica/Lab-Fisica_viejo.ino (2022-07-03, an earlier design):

/*
/////////////////////
Procedimiento:
Enviar GET (para saber estado actual)
Enviar POST(para asignar datos)
Arduino responde  "HTTP/1.1 200 OK"
luego enviar GET hasta que arduino responda(si no se conecta es porque está trabajando en el pedido del post)
*/
#include <Arduino.h>
#include <ArduinoJson.h>
#include <UIPEthernet.h>
#include <Servo.h>

#define const_status 500
#define const_instruc 500

static byte mymac[] = {0xDE, 0xAD, 0xBE, 0xEF, 0xFE, 0xED};
static byte myip[] = {172,20,5,140};
byte Ethernet::buffer[const_status];
//--------- Declaración de variables ----------//
//---- VAriables de json ----// (GENERICO)
// Estado
int num_Lab=0;
bool subLab=0;
bool iniLab=1;
// Analogico
int Analogico_0=0;
int Analogico_1=0;
int Analogico_2=0;
int Analogico_3=0;
int Analogico_4=0;
//--- Variables auxiliares ---//
int distancia_act_1; //Distancias actuales de cada motor
int distancia_act_2;
int distancia_act_3;
int dist_mov; // distancia que se debe mover el motor en realidad
bool bandera=0;

//---------- Funciones  ---------------//
/**
 * @brief 
 * 
 * @param diafragma 
 * @param cant_med 
 * @param distancia_fl 
 * @param distancia_lp 
 */
void Convergentes(int diafragma, int cant_med, int distancia_fl, int distancia_lp);
void Divergentes(int diafragma, int cant_med, int distancia_fl1, int distancia_l1l2, int distancia_l2p);
void Control_Motor(int motor, int distancia);
bool control_distancia(int distancia_act, int distancia);
int  Mover_Motor(int bobina_1, int bobina_2, int bobina_3, int bobina_4, int dist_mov, int aux_dist, bool sentido);
void valorSalidas(int selector,int bobina_1, int bobina_2, int bobina_3, int bobina_4);
void stopMotor(int bobina_1, int bobina_2, int bobina_3, int bobina_4);

//////////// declaración de salidas ///////////////////
//---------------- Motores --------------------------//
// Motor 1
#define IN1_1  6
#define IN2_1  7
#define IN3_1  8
#define IN4_1  9
// Motor 2
#define IN1_2  20
#define IN2_2  21
#define IN3_2  22
#define IN4_2  23
// Motor 3
#define IN1_3  24
#define IN2_3  25
#define IN3_3  26
#define IN4_3  27
// Leds
#define Led_M1 10
#define Led_M2 11
#define Led_M3 12
#define Led_aux 13
#define Led_S1 2
#define Led_S2 3
// Foco
#define Foco_pin 28
// Servo Diafragma
#define Diafragma_pin 4
// Servo Lente
#define Lente_pin 5
// Declaramos la variable para controlar el servo
Servo servo_diafragma;
Servo servo_lente;
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

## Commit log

2022-04-28 Agregado de imagenes al readme.md
2022-04-28 unificacion de criterios
2022-05-05 Orden y adaptación de salidas y funciones
2022-05-05 Optimización de funciones y control de envio y recepcion de Json
2022-05-05 Movimiento de Motor resuelto Ver reporte de vueltas para analizar estado actual.
2022-05-05 Control de servo realizado Ya realiza el conteo de vueltas
2022-05-05 Surge un problema en Arduino UNO Cuando se usa casi el 90% de la memoria se traba en algunos procesos.
    controlar el GET
2022-05-06 Programación del arduino desde VSCode
2022-05-06 ajustes de funciones get y post Controlar las distancias de cada motor.
2022-05-09 Definición de distancias máx y mín
2022-05-09 Control de distancias solucionado
2022-05-11 Ajustes de pines para Arduino Mega
2022-05-27 carga de esquematico tentativo
2022-05-27 Incorporación Archivos esquematicos
    [lab_fisica.brd, lab_fisica.sch]
2022-05-31 Carga de diseños pcb
    [Diseño de FISICA v2.f3z]
2022-05-31 PCB casi terminado - Controlar y corregir
    [Diseño de FISICA v8.f3z]
2022-06-02 PDF of schematic and board
2022-06-02 Protocolo de comunicación Programa usado para controlar las formas de comunicación
2022-06-03 Control de protocolo con nueva librería
2022-06-06 Diseño de control generico terminado.
2022-06-06 Lab-Fisica protocolo actualizado. Control de movimiento
2022-06-16 Protocolo - Pruebas con Ethercard y el diseño del programa
2022-07-01 Prueba de webSocket
2022-07-01 Pruebas de WebSocket Quizas no sirve para lo que necesitamos
2022-07-03 Protocolo de comunicación Se realizó la actualización del protocolo de comunicación
2022-07-04 Programa funcionando Queda corregir algunos detalles del control de distancias y las banderas
2022-07-05 Actualización de Protocolo Está funcionando el programa para arduino. y el protocolo de comunicación. No se desconecta.
2022-07-06 cambios en esquematico y pcb
    [Diseño de FISICA v19.f3z]
2022-07-12 esquematico y board exportados
    [Diseño_de_FISICA_v14.sch, Diseño_de_FISICA_v17.brd]
2022-07-13 esquematico actualizado
    [Diseño_de_FISICA_v15.sch]
2022-07-13 export sch
    [Diseño_de_FISICA_v16.sch]
2022-07-14 Actualización de descripciones Se actualizaron las descripciones de las funciones y detalles
2022-07-14 Actualización readme y esquematico
    [Diseño_de_FISICA_v14.sch]
2022-07-21 Primera PCB
    [Diseño_de_FISICA_v16.brd]
2022-07-21 Acualización PCB y SCH
    [Diseño_de_FISICA_v16.brd]
2022-09-13 cambios PCB
    [Diseño_de_FISICA_v16.brd, Diseño_de_FISICA_v16.sch]
2022-09-14 Actualización de manejo de motores Pruebas con servos
2022-09-15 modificación esquematico
    [Diseño_de_FISICA_v16.brd, Diseño_de_FISICA_v16.sch]
2022-09-15 Modif PCB
    [Diseño_de_FISICA_v16.brd, Diseño_de_FISICA_v16.sch]
2022-09-16 PCB Corregidas
    [Diseño_de_FISICA_v16.brd, Diseño_de_FISICA_v16.sch]
2022-09-16 Diseño PCB full
    [Diseño_de_FISICA_v16.brd, Diseño_de_FISICA_v16.sch]
2022-09-16 Correcciones PCB
    [Barra_10x4.skp, Barra_15x4.skp, Barra_15x4.stl, Diseño_de_FISICA_v16.brd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]
2022-09-16 diseños 3d
    [Barra_10x4_V2.skp]
2022-09-18 Modificaciones para control de distancias y readme
2022-09-19 diseño 3D SisCom
    [BarraInterna.skp, BarraInterna.stl, Barra_10x4_LyD.skp, Barra_10x4_LyD.stl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]
2022-09-20 Ultimos detalles motorees
2022-09-20 Ajuste pos inicial de servos en 90. Actualizacion de imagenes de placa
2022-09-21 NuevosDiseños 3D
    [Barra_15x4.skp, Caja.skp, Caja.stl, CajaCompleto.skp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]
2022-09-22 impresiones 3d - ver motores cuando cambian juntos
    [14b+engranaje+45+dientes.skp, Barra_10x4_LyD.skp, diafragma-con-engranaje.stl]
2022-09-22 Diseños_3D
    [Difusor.skp, Difusor.stl, LuzCompleta.skp, LuzFrente.skp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]
2022-09-29 Diseños3D
    [LuzBarra.skp, LuzBarra.stl, TelecoServo.skp, TelecoServo.stl]
2022-11-23 Agregados de imagenes y actualización Readme.md
2022-11-24 cambios en readme.md actualización de imagenes
